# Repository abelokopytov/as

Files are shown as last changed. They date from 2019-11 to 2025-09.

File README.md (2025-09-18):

# as
Construction of prototype free-view extra cheap substitution anomaloscope.

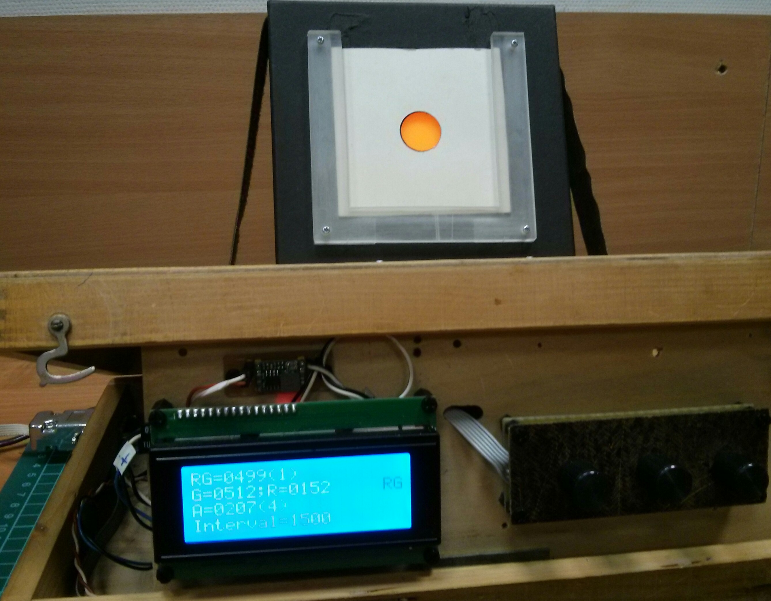
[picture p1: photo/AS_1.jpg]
General view of the device


The device consists of control box and stimulus box.

Control box is arduino based.
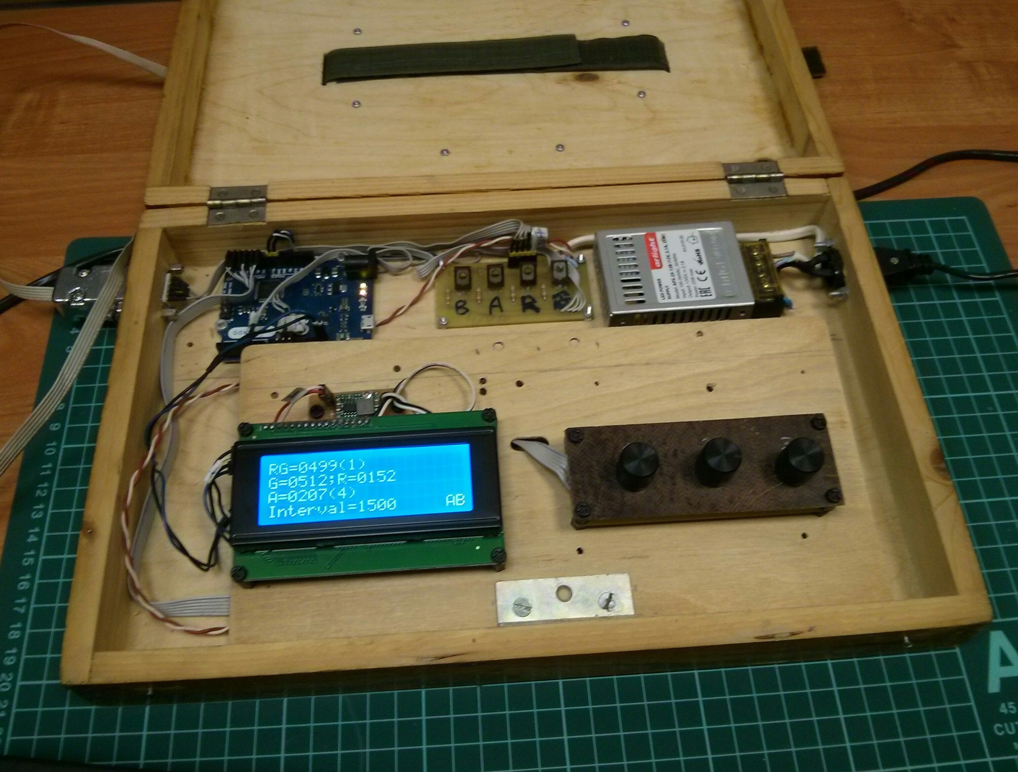
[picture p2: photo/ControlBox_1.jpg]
Inside control Box


Arduino Leonardo was used to provide at least 3 PWM channels with 16-bit resolution.

Power supply is DC 12V 2A.

Three encoders were connected to arduino with common bus method (https://github.com/j-bellavance/CommonBusEncoders).

LCD display is 2004 with I2C interface. DC-DC convertor from 12V to 5V was used for display backlight.

Output bi-polar NPN old soviet KT961Б transistors (but one can use MOSFET) are mounted on "power pcb".

Wiring of parts to Leonardo can be seen from software source code.

Software sources for control box are in /src folder.

as.ino sketch provides alternation of RG mixture field and A (Amber == Yellow) field with interval of 1.5 sec.

dimmer.ino sketch provides static fields presentation for spectral measurements.

PCBs were developed with [Fritzing](https://fritzing.org). Fritzing files and PCB images are in /pcb folder.

One-sided PCBs were made with LUT technology (laser printer + iron).

Stimulus box is black cartoon box of 14X14X5 cm.
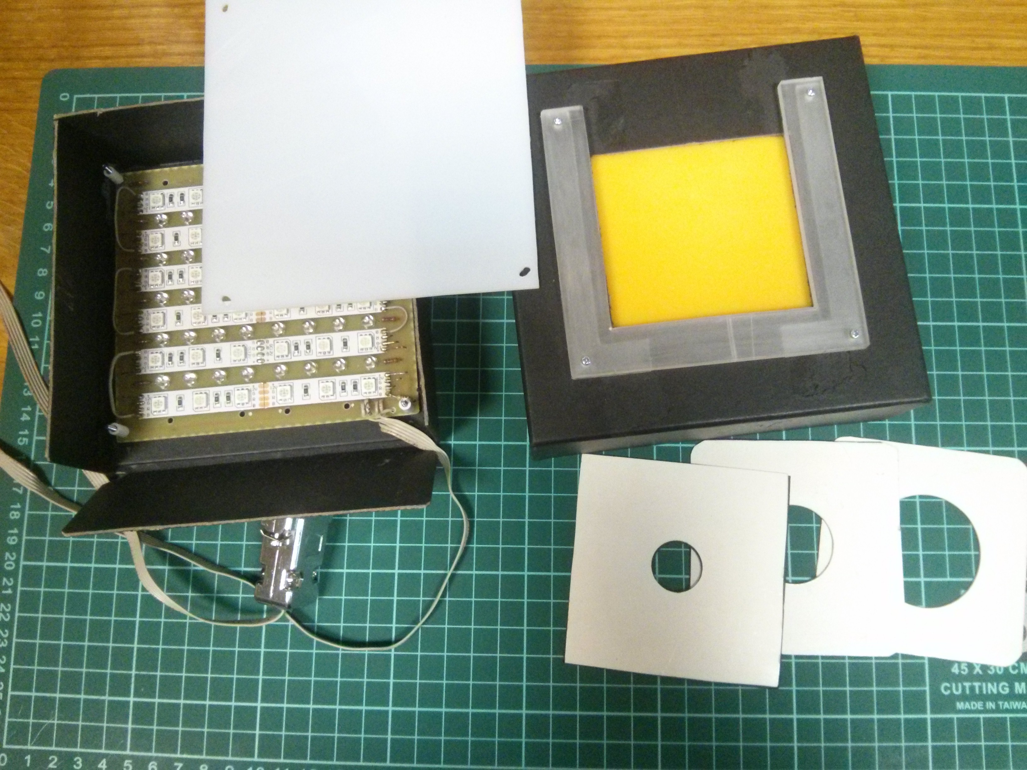
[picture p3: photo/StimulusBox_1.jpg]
Stimulus box


For RG field 12V RGB led strip was used with 5050 smd leds, 60 per meter, 14W/m power ([Arlight](https://arlight.ru)),
but one can use analogoues strips.

For Amber field wide angle "straw-hat" leds from aliexpress were used.

Spectral measurements were done with X-Rite Eye One spectrophotometer in hi-res mode.

Peak inensities of the leds are: R - 620 nm, G - 520 nm, A - 590 nm.

To eliminate blue cone excitation it is nessesary to use green light > 540 nm.
As there are no commercially available bright green leds with peak wavelength of 550 nm, we
filter out radiation less than 540 nm with 6 layers of the yellow cellophane paper ([Sadipal](https://sadipal.com) Ref. 06162 Amarillo).

The plate was mounted on the back side of stimulus box cover.

Another white opale plastic plate was mounted on PCB above leds.

Such construction provides good uniformity of fields.

Stimulus box was equipped with exchangeable diaphragms with 2, 3 or 4 cm circular windows.

The simplicity and cheapness of the project makes it affordable for students.

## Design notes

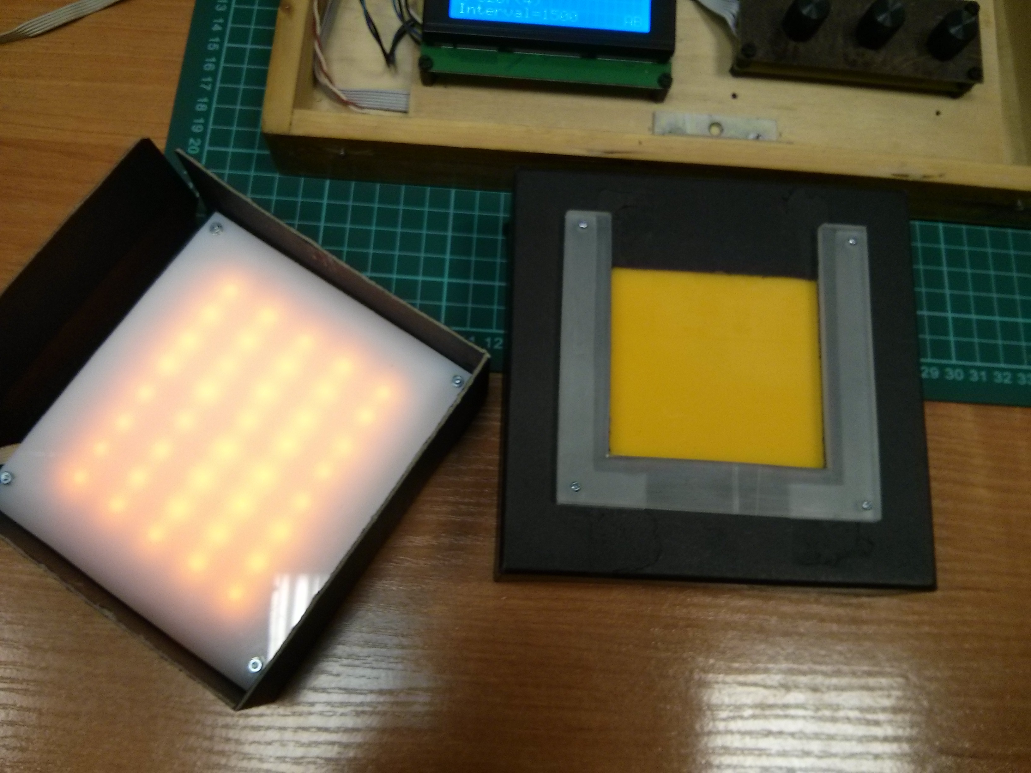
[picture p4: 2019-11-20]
photo/StimulusBox_3.jpg

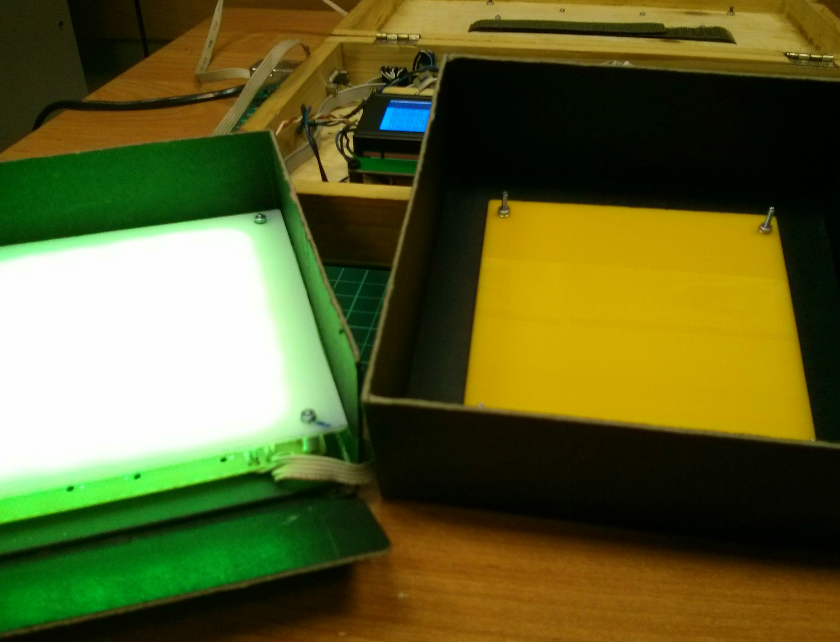
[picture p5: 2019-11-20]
photo/StimulusBox_4.jpg

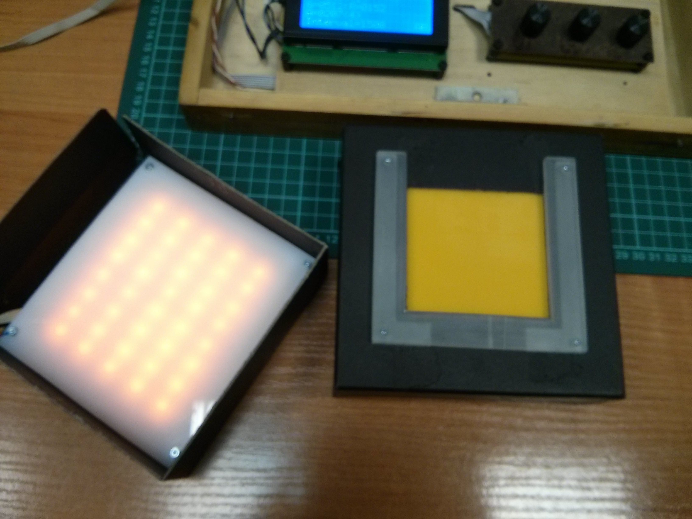
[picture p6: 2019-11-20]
photo/StimulusBox_2.jpg

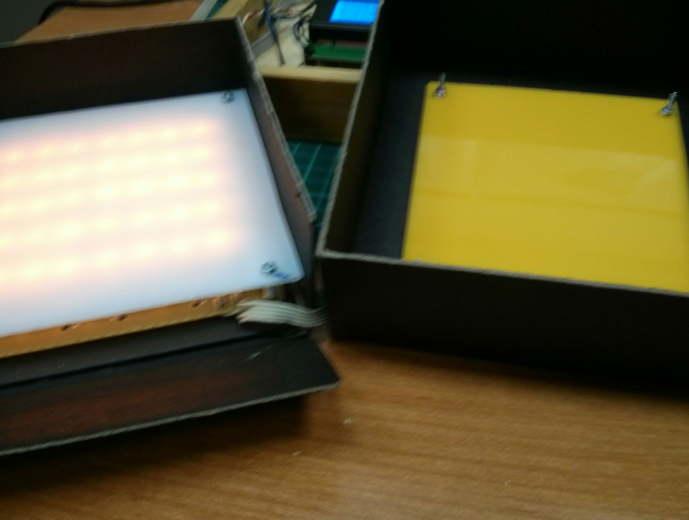
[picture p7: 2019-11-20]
photo/StimulusBox_5.jpg

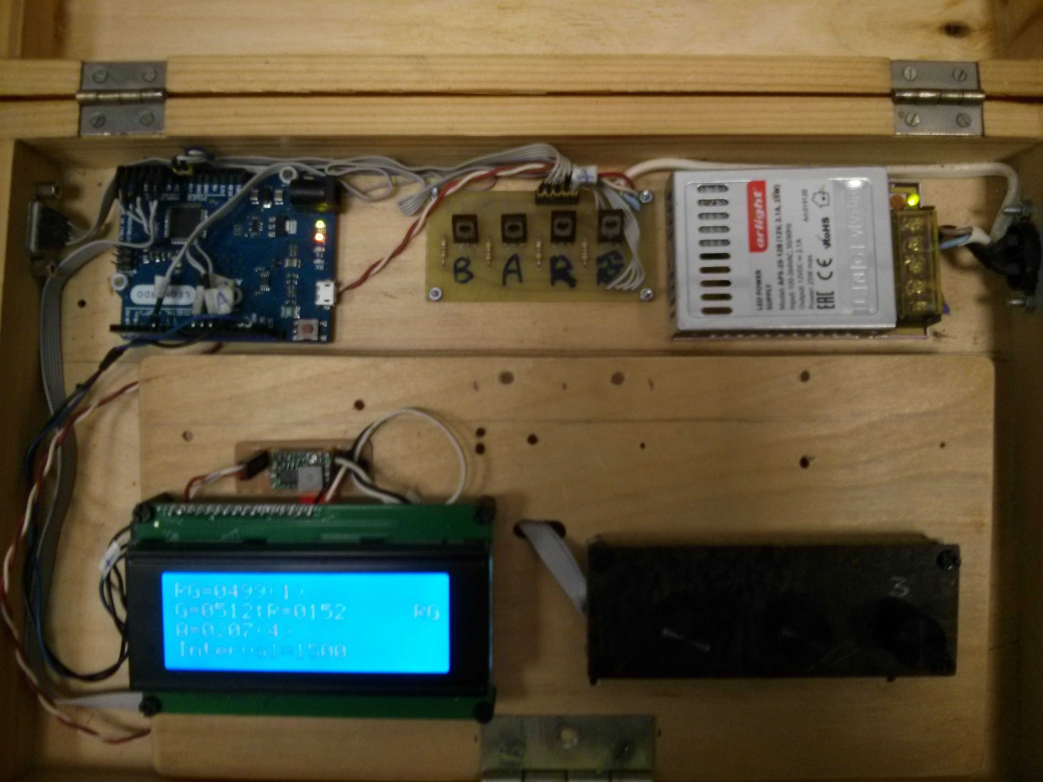
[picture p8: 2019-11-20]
photo/ControlBox_2.jpg

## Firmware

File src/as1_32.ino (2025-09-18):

// ######################################################
#define VERSION "as1_32 16-bit"

// Cellophan filter 6 layers
// Thick common wire
// 16-bit

//for LCD 20x4 I2C
#include <Wire.h>
#include <hd44780.h>
#include <hd44780ioClass/hd44780_I2Cexp.h>
// declare the lcd object
hd44780_I2Cexp lcd; // auto locate and autoconfig interface pins
// tell the hd44780 sketch the lcd object has been declared
#define HD44780_LCDOBJECT
#define LCD_COLS 20
#define LCD_ROWS 4

//for DS18B20 temperature sensor
#include <OneWire.h> 
#include <DallasTemperature.h>
#define ONE_WIRE_BUS 12 // pin 12
OneWire oneWire(ONE_WIRE_BUS); 
DallasTemperature dtemp(&oneWire);

//https://github.com/j-bellavance/CommonBusEncoders
#include <CommonBusEncoders.h>
//encoders(BusA, BusB, BusSwitches, Number of encoders)
CommonBusEncoders encoders(A0, A1, A2, 3);

#include "SoftwareSerial.h"
#include "DFRobotDFPlayerMini.h"
SoftwareSerial mySoftwareSerial(8, 6); // RX, TX  - to communicate with DFPlayerMini
DFRobotDFPlayerMini myDFPlayer;

// from https://github.com/jfturcot/SimpleTimer
#include <SimpleTimer.h>
// There must be one global SimpleTimer object.
SimpleTimer timer;
int timerId;
int timerInterval = 1500; // 1,5 sec
bool autoChangePhase = true;

// Encoder 1
float    rgRatio;
float    rgStepSmall  = 0.001;
float    rgStepMedium = 0.01;
float    rgStepBig    = 0.1;
float    rgStep  = rgStepSmall;

// Encoder 2
unsigned int stepAmberSmall  =  16;
unsigned int stepAmberMedium =  64;
unsigned int stepAmberBig    = 256;
unsigned int stepAmber = stepAmberSmall;

//Encoder 3
float    stepLum = 1.0;

//const unsigned int maxValue =  1023; //10-bit resolution
const unsigned long maxValue =  65535; //16-bit resolution

//Pins
int pinGreen = 10;
int pinRed   =  9;
int pinAmber =  11;
int pinBlue  =  5;

unsigned long valueRed = 0;
unsigned long valueGreen = 0;
unsigned long valueAmber = 0;
unsigned long valueBlue = 0;

unsigned long maxValueRed;
unsigned long maxValueGreen = maxValue; //65535


//AS1 with SB1+cellophan filter 6 layers
// from spectra measurements 17.09.2024
// max Green Luminance 35.87 cd/m2
// max Red   Luminance 155.1 cd/m2
float maxLumGreen = 35.9; // boundary value -- cd/m2
float maxLumRed = 155.1;  // not used -- cd/m2

// For Luminance = 20 cd/m2 Red and Green values were defined by spectral measurements
float valueLum = 20.0;
// Measurements 2025.02.26 
//unsigned long valueGreenLum20 = 34500;
//unsigned long valueRedLum20 = 7450;
//unsigned long valueAmberLum20 = 11800;

// Measurements 2025.06.20 T=25.0
unsigned long valueGreenLum20 = 39200; //Yxy: 20.033197 0.355382 0.631694
unsigned long valueRedLum20 = 7810;    //Yxy: 20.051561 0.691100 0.308226
//unsigned long valueAmberLum20 = 11500; //Yxy: 20.022201 0.563441 0.435640
// Measurements 2025.06.23
// G=39200 Y=20.83 T=24.0; R=7810 Y=20.51 T=24.0; A=11500 Y=18.71 T=23.0
// increase A
//unsigned long valueAmberLum20 = 12500; //Yxy: 20.453128 0.561619 0.436786
// Measurements 2025.06.25
// G=39200 Y: 20.601455 T=24.4; R=7810 Y: 20.187054 T=24.6; A:12500 Y=18.851710 T=24.3
// increase A
unsigned long valueAmberLum20 = 13300; //Yxy: 20.872399 0.562126 0.435786 T=24.3


bool flagShowFlipFlop = true;

int phase = 0;

float fTemp; // Temperature

int mode = 0; // mode of operation == screen

//######################################
// Configure digital pins 9, 10, 11 as 10-bit PWM outputs. Freq = 976Hz
void setupPWM10() {
  DDRB  |= _BV(PB5) | _BV(PB6) | _BV(PB7); //pins 9,10,11
  TCCR1A = _BV(COM1A1) | _BV(COM1B1) | _BV(COM1C1) /* non-inverting PWM */
        | _BV(WGM11) | _BV(WGM10);                 /* mode 3: Phase correct, 10-bit */

  TCCR1B = _BV(CS11); //prescaler=8

  DDRC  |= _BV(PC6); //pin5
  TCCR3A = _BV(COM3A1) /* non-inverting PWM */
        | _BV(WGM31) | _BV(WGM30);                 /* mode 3: Phase correct, 10-bit */
  TCCR3B = _BV(CS31); //prescaler=8
}
//######################################
// Configure digital pins 9, 10, 11, and 5 as 16-bit PWM outputs. Freq = 244 Hz
void setupPWM16() { 
  DDRB  |= _BV(PB5) | _BV(PB6) | _BV(PB7);
  TCCR1A = _BV(COM1A1) | _BV(COM1B1) | _BV(COM1C1) /* non-inverting PWM */
        | _BV(WGM11);                 /* mode 14: fast PWM, TOP=ICR1 */
  TCCR1B = _BV(WGM13) | _BV(WGM12) | _BV(CS10); //prescaler=1
  ICR1 = 0xFFFF;

  DDRC  |= _BV(PC6); //pin5
  TCCR3A = _BV(COM3A1) /* non-inverting PWM */
        | _BV(WGM31);                 /* mode 14: fast PWM, TOP=ICR1 */
  TCCR3B = _BV(WGM33) | _BV(WGM32) | _BV(CS30); //prescaler=1
  ICR3 = 0xFFFF;
}
//######################################
/* 16-bit version of analogWrite(). Works only on pins 9, 10, 11, 5 */
void analogWriteHR(int pin, unsigned int val) {
  switch (pin) {
    case  9: OCR1A = val; break; //Red
    case 10: OCR1B = val; break; //Green
    case 11: OCR1C = val; break; //Amber
    case  5: OCR3A = val; break; //Blue
  }
}
//######################################
String numToStrLen(unsigned int n, int len) {
  String result = "";
  for (int pos=1; pos < len; pos++) {
    if (n < pow(10, pos)) result += "0";
  }
  result += n;
  return result;
}
//####################################################################
void setup() {
    Serial.begin(115200);
    mySoftwareSerial.begin(9600); // for myDFPlayer
    delay(5000);
  
    lcd.begin(LCD_COLS, LCD_ROWS);
    lcd.clear();
    lcd.setCursor(0, 0);
    lcd.print(String(VERSION));
    delay(5000);
    lcd.clear();

    delay(5000);
    while (!myDFPlayer.begin(mySoftwareSerial)) {  //Use softwareSerial to communicate with mp3.
        Serial.println(F("Unable to begin:"));
        Serial.println(F("1.Please recheck the connection!"));
        Serial.println(F("2.Please insert the SD card!"));
        delay(5000); // Code to compatible with ESP8266 watch dog.
    }
    delay(5000);
    myDFPlayer.volume(20);  //Set volume value. From 0 to 30

    dtemp.begin();
    dtemp.setWaitForConversion(false); //non-blocking
    dtemp.requestTemperatures();

    encoders.setDebounce(16);
    // addEncoder(Encoder number, 4 steps per click, pin, number of modes, returned code, returned switch code )
    encoders.addEncoder(1, 4, A3, 1, 100,   1); // set RG
    encoders.addEncoder(2, 4, A4, 1, 200,   2); // set Amber
    encoders.addEncoder(3, 4, A5, 3, 300,   3); // change mode

  
    timerId = timer.setInterval(timerInterval, writeStimulus);

    //initial values for normal trichromat
    rgRatio = 0.402;  // R/G ratio
    valueAmber = valueAmberLum20;
    
    setupPWM16();
    analogWriteHR(pinBlue, 0);
  
    calcRG();
    displayVars();
}
//############################
void displayVars() {
    lcd.setCursor(14, 0);
    if (mode == 0)      lcd.print("Main  ");
    else if (mode == 1) lcd.print("SetLum ");
    else if (mode == 2) lcd.print("Static");

    lcd.setCursor(0, 0);
    lcd.print("RG=" + numToStrLen((int)(1000.0 * rgRatio), 4) + "(." + numToStrLen((int)1000.0*rgStep, 3) + ")");
    lcd.setCursor(0, 1);
    lcd.print("G=" + numToStrLen(valueGreen, 5) +  ";R=" + numToStrLen(valueRed, 5));
    lcd.setCursor(0, 2);
    lcd.print("A=" + numToStrLen(valueAmber, 5) + "(" + numToStrLen(stepAmber, 3) + ")");
    lcd.setCursor(13, 2);
    lcd.print("Lum=" + numToStrLen((int)1.0*valueLum, 2));

    lcd.setCursor(0, 3);
    lcd.print(String("Int=") + timerInterval + String("  "));
}
//####################################################################
void displayTemp() {
    lcd.setCursor(9, 3);
    lcd.print("T=" + String(fTemp) + (char)223); // 223 - Celsius
}
//############################
void calcRG() { // given rgRatio, Lum, calculate valueRed, valueGreen
    valueRed = (unsigned long)((float)rgRatio*valueLum/20.0*valueRedLum20);
    if (valueRed > maxValue) valueRed = maxValue;
    valueGreen = (unsigned long)((float)(1.0 - rgRatio)*valueLum/20.0*valueGreenLum20);
    if (valueGreen > maxValue) valueGreen = maxValue;
}
//############################
void writeStimulus() {
    if (autoChangePhase)
        phase = 1 - phase;
    if (phase == 0) {
      if (flagShowFlipFlop) {
          lcd.setCursor(18, 1);
          lcd.print("RG");
          lcd.setCursor(18, 3);
          lcd.print("  ");
          lcd.display();
      }
      analogWriteHR(pinRed,   valueRed);
      analogWriteHR(pinGreen, valueGreen);
      analogWriteHR(pinAmber, 0);
    }
    if (phase == 1) {
        if (flagShowFlipFlop) {
            lcd.setCursor(18, 1);
            lcd.print("  ");
            lcd.setCursor(18, 3);
            lcd.print("Am");
            lcd.display();
            if (mode != 2) myDFPlayer.play(1);  //Play the first mp3
        }
        analogWriteHR(pinRed,   0);
        analogWriteHR(pinGreen, 0);
        analogWriteHR(pinAmber, valueAmber);
    }
}
//############################
void changeTimerInterval() {
    switch (timerInterval) {
        case 1500: {
            timerInterval = 500;
            flagShowFlipFlop = true;
            break;
        }
        case  500: {
            timerInterval = 100;
            flagShowFlipFlop = false;
            lcd.setCursor(18, 1); lcd.print("  ");
            lcd.setCursor(18, 3); lcd.print("  ");
            lcd.display();
            break;
        }
        case  100: {
            timerInterval = 1500;
            flagShowFlipFlop = true;
        }
    }
    timer.deleteTimer(timerId);
    timerId = timer.setInterval(timerInterval, writeStimulus);
}
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

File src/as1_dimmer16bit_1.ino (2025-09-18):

#define VERSION "as1_dimmer16bit_1"

//for LCD 20x4 I2C
#include <Wire.h>
#include <hd44780.h>
#include <hd44780ioClass/hd44780_I2Cexp.h>
// declare the lcd object
hd44780_I2Cexp lcd; // auto locate and autoconfig interface pins
// tell the hd44780 sketch the lcd object has been declared
#define HD44780_LCDOBJECT
#define LCD_COLS 20
#define LCD_ROWS 4

//for DS18B20 temperature sensor
#include <OneWire.h> 
#include <DallasTemperature.h>
#define ONE_WIRE_BUS 12 // pin 12
OneWire oneWire(ONE_WIRE_BUS); 
DallasTemperature dtemp(&oneWire);

//https://github.com/j-bellavance/CommonBusEncoders
#include <CommonBusEncoders.h>
//encoders(BusA, BusB,BusSwitches, Number of encoders)
CommonBusEncoders encoders(A0, A1, A2, 3);

//-------------------------------------------
const unsigned long maxValue =  65535; //16-bit resolution

unsigned int stepTiny     =    1;
unsigned int stepSmall    =    4;
unsigned int stepBig      =   16;
unsigned int stepExtraBig =  256;
unsigned int stepHuge     = 1024;

struct colorStruct {
  int pin;
  char name[6];
  unsigned long value;
  unsigned int step;
};

#define NUM_COLORS 4
struct colorStruct colors[NUM_COLORS] = {
{ 9, "Red  ", 0, stepExtraBig},
{10, "Green", 0, stepExtraBig},
{ 5, "Blue ", 0, stepExtraBig},
{11, "Amber", 0, stepExtraBig}
};

int colorIndex = 0;
struct colorStruct color = colors[colorIndex];

float fTemp;

// Configure digital pins 9, 10, 11, 5 as 10-bit PWM outputs. Freq = 976Hz -- Arduino Leonardo --
void setupPWM10() {
  DDRB  |= _BV(PB5) | _BV(PB6) | _BV(PB7); //pins 9,10,11
  TCCR1A = _BV(COM1A1) | _BV(COM1B1) | _BV(COM1C1) /* non-inverting PWM */
        | _BV(WGM11) | _BV(WGM10);                 /* mode 3: Phase correct, 10-bit */

  TCCR1B = _BV(CS11); //prescaler=8

  DDRC  |= _BV(PC6); //pin5
  TCCR3A = _BV(COM3A1)                             /* non-inverting PWM */
        | _BV(WGM31) | _BV(WGM30);                 /* mode 3: Phase correct, 10-bit */
  TCCR3B = _BV(CS31); //prescaler=8
}
// Configure digital pins 9, 10, 11, and 5 as 16-bit PWM outputs. Freq = 244 Hz -- Arduino Leonardo --
void setupPWM16() {
  DDRB  |= _BV(PB5) | _BV(PB6) | _BV(PB7); //pins 9,10,11
  TCCR1A = _BV(COM1A1) | _BV(COM1B1) | _BV(COM1C1) /* non-inverting PWM */
         | _BV(WGM11);                 /* mode 14: fast PWM, TOP=ICR1 */
  TCCR1B = _BV(WGM13) | _BV(WGM12) | _BV(CS10); //prescaler=1
  ICR1 = 0xFFFF;

  DDRC  |= _BV(PC6); //pin5
  TCCR3A = _BV(COM3A1) /* non-inverting PWM */
        | _BV(WGM11);                 /* mode 14: fast PWM, TOP=ICR1 */
  TCCR3B = _BV(WGM33) | _BV(WGM32) | _BV(CS30); //prescaler=1
  ICR3 = 0xFFFF;
}
/* HR-bit version of analogWrite(). Works only on pins 9, 10, 11, 5 */
void analogWriteHR(int pin, unsigned int val) {
  switch (pin) {
    case  9: OCR1A = val; break; //Red
    case 10: OCR1B = val; break; //Green
    case 11: OCR1C = val; break; //Amber
    case  5: OCR3A = val; break; //Blue
  }
}
//####################################################################
void setup() {
  //Serial.begin(115200);

  lcd.begin(LCD_COLS, LCD_ROWS);
  lcd.clear();
  lcd.setCursor(0, 0);
  lcd.print(String(VERSION));
  delay(5000);
  lcd.clear();

  dtemp.begin();
  dtemp.setWaitForConversion(false); //non-blocking
  dtemp.requestTemperatures();

  encoders.setDebounce(16);
  // addEncoder(Encoder number, steps per click=4, pin, number of modes=1, returned code, returned switch code )
  encoders.addEncoder(1, 4, A3, 1, 100,   1);
  encoders.addEncoder(2, 4, A4, 1, 200,   2);
  encoders.addEncoder(3, 4, A5, 1, 300,   3);

  setupPWM16();
  for(int i=0; i<NUM_COLORS; i++) {
    analogWriteHR(colors[i].pin, 0);
  }
  displayRGBA();
}
//######################################
String numToStrLen(unsigned int n, int len) {
  String result = "";
  for (int pos=1; pos < len; pos++) {
    if (n < pow(10, pos)) result += "0";
  }
  result += n;
  return result;
}
//####################################################################
void displayRGBA() {
  analogWriteHR(color.pin, color.value);
//  lcd.clear();
  lcd.setCursor(0, 0);
  lcd.print("R=" + numToStrLen(colors[0].value, 5) + "(" + numToStrLen(colors[0].step, 4) + ")");
  lcd.setCursor(0, 1);
  lcd.print("G=" + numToStrLen(colors[1].value, 5) + "(" + numToStrLen(colors[1].step, 4) + ")");
  lcd.setCursor(0, 2);
  lcd.print("B=" + numToStrLen(colors[2].value, 5) + "(" + numToStrLen(colors[2].step, 4) + ")");
  lcd.setCursor(0, 3);
  lcd.print("A=" + numToStrLen(colors[3].value, 5) + "(" + numToStrLen(colors[3].step, 4) + ")");

  lcd.setCursor(14, 0);
  lcd.print("Color=");
  lcd.setCursor(15, 1);
  lcd.print(color.name);
}
//####################################################################
void displayTemp() {
  lcd.setCursor(13, 3);
//  lcd.print(String("T=") + String(fTemp) + (char)223);
  lcd.print(String("T=") + String(fTemp));
}
//####################################################################
unsigned int getNextStep(unsigned int step) { 
  if (step == stepTiny)
     step = stepSmall;
  else if (step == stepSmall)
     step = stepBig;
  else if (step == stepBig)
     step = stepExtraBig;
  else if (step == stepExtraBig)
     step = stepHuge;
  else if (step == stepHuge)
     step = stepTiny;
  return step;
}
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
